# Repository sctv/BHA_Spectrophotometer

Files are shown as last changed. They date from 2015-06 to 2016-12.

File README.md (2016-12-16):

#BHA Spectrophotometer

This repo contains the designs and source files of a **DIY Spectrophotometer**. This device, based on the TSL1402R IC, can be used to do a photospectral analysis of liquid samples, such as growth curve analysis. Check out the corresponding [BHA lecture in the Syllabus](http://biohackacademy.github.io) for more information.

##Navigation the repo

 	BHA_Spectrophotometer/					main repo
 	|-- Arduino Code/Spectrophotometer/		Arduino Code
 	|-- Assembly/							Assembly guide
 	|-- Processing Code						Processing User interface code
 	BoM.md									Bill of Materials
 	Iodine Clock Reaction.pdf				Tutorial
 	Spectrophotometer-Cut-Sheet.svg			Laser cut sheet
 	Spectrophotometer-Fritzing.fzz			Wiring source
 	Spectrophotometer-Sketchup.skp			3D model
 	
##Releases

The BioHack Academy 3 release contains the following:

* 2015 BHA1 Design
* 2015 BHA2 Design
* 2016 BHA3 Design

## To Do

The To Do's are tracked using the Issues section. Please maket more suggestions by posting there.

## License

All code is licensed under GNU General Public License.

All designs are licensed under Creative Commons Contribution Share-Alike license

Copyright Waag Society

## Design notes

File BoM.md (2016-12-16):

## Bill of Materials

Make sure you have an Arduino Leonardo or equivalent microprocessor, big enough sheets of 3mm material to cut the design from and plenty of wires and M3 10 screws and nuts to assemble all the parts.

### Must have for photodiode array design

For this device you need an Arduino or equivalent microprocessor.

|No|Amount|Description|Supplier NL|Cost|
| ------------: | ------------: | :------------ | :------------ | ------------: |
|1|1|White 5mm LED|[iPrototype](https://iprototype.nl/products/components/led-lcd/ledwit), [EOO](http://www.eoo-bv.nl/index.php?_a=viewProd&productId=9088), [Hackerstore](https://www.hackerstore.nl/Artikel/257)|0.18|
|2|1|TSL1406R Photo diode array|[Mouser](http://nl.mouser.com/ProductDetail/ams/TSL1406R/?qs=owm69ILshgasXOGrAzFz%252bQ%3D%3D), [DigiKey](http://www.digikey.nl/product-detail/en/TSL1406R/TSL1406-R-ND/3095064)|22.57|
|3|1|1,000 lines/mm grating|[ipacity](http://ipacity.biedmeer.nl/Webwinkel-Product-78540591/Folie-tralie-1000-lijnen-mm-%2815-x-30-cm%29.html), [Carolina](http://www.carolina.com/physical-science-light-and-optics/diffraction-grating/755230.pr?catId=&mCat=&sCat=&ssCat=&question=diffraction+grating)|14.00|
|4|1|100 uF capacitor|[Farnell](http://nl.farnell.com/panasonic-electronic-components/eeufr1c101/cap-alu-elec-100uf-16v-rad/dp/1907228)|0.14|
|5|4|220 ohm resistor|[Farnell](http://nl.farnell.com/multicomp/mcf-0-25w-220r/resistor-carbon-film-220r-0-25w/dp/9339299?Ntt=9339299), [iPrototype](https://iprototype.nl/products/components/resistors/220R), [EOO](http://www.eoo-bv.nl/index.php?_a=viewProd&productId=7085)|0.02|
|6|1|Array of 13 right angle header pins|[iPrototype](https://iprototype.nl/products/accessoires/headers/header-male-right-angle)|0.99|
|7|1|RGB LED|[Farnell](http://nl.farnell.com/kingbright/l-154a4surkqbdzgw/led-multi-colour-rgb-5mm/dp/2290374), [iPrototype](https://iprototype.nl/products/components/led-lcd/rgbled)|0.95|

*Estimate cost*: EUR 38.85

**Alternatives**

* Photodiode arrays can be found in flat bed scanners
* CCD chips are part of cheap webcams
* Compact Discs (CDs) have 0.001 mm slits

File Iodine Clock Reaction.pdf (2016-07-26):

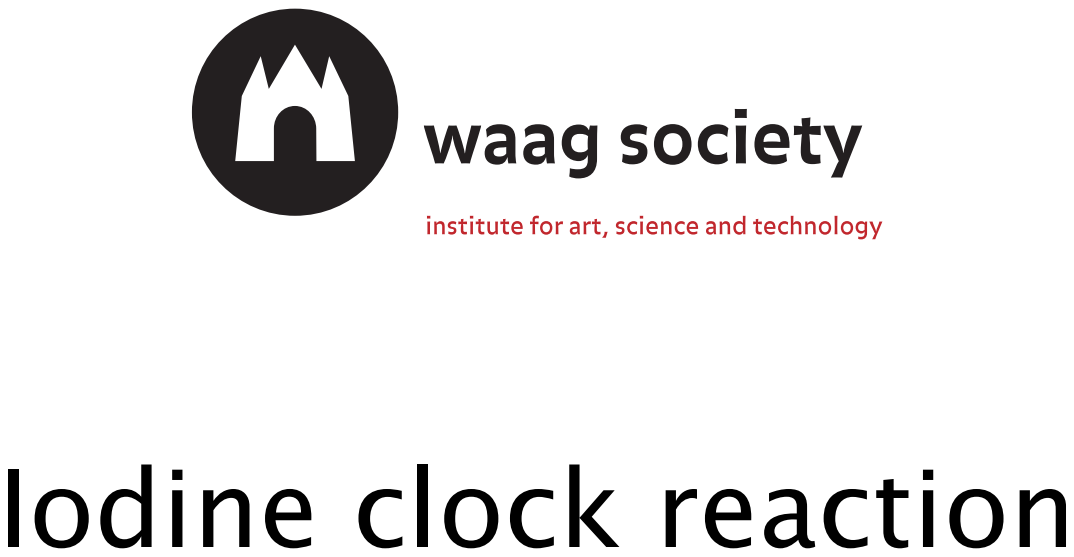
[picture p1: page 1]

Iodine clock reaction

## Consumables and Equipment

- 4x 50 mL tube
- 1000 mg Vitamin C tablet (you can also use two 500mg of course)
- Iodine (2%) availabe at a drug store
- Hydrogen peroxide (3%) also from a drug store
- Liquid Starch Solution (0.3%, so 3 grams of starch in 1 liter of heated water)
- Warm water
- Pipettes
- Plastic bag
- Safety goggles
- Marker

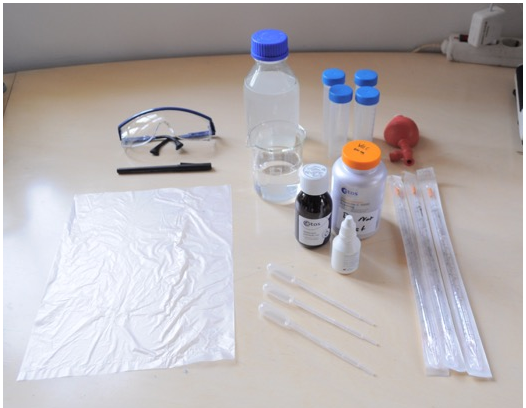
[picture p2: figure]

## Iodine clock reaction

Put on those safety goggles

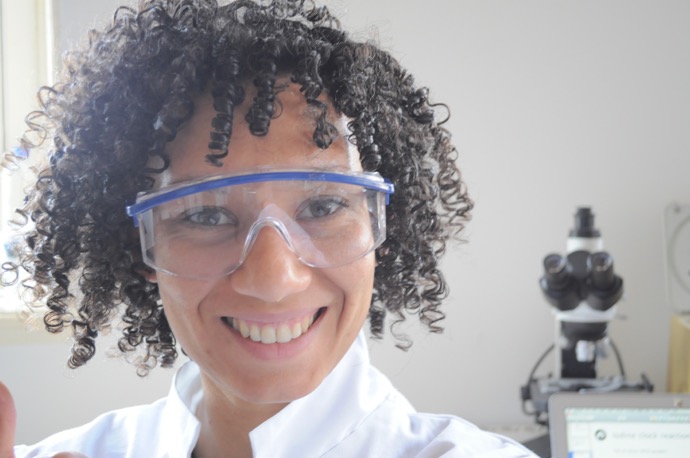
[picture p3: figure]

## Iodine clock reaction

Crush the Vitamin C tablet in a plastic bag

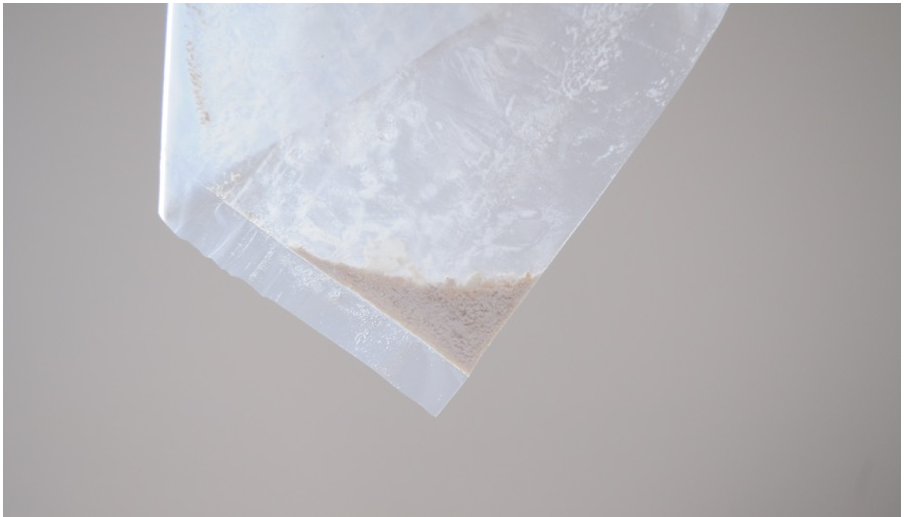
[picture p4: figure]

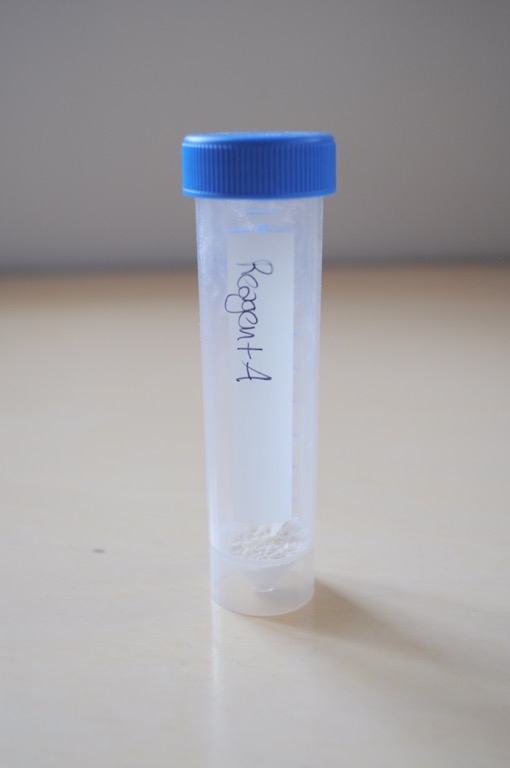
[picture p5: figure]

- Put the powder in a 50 mL tube
- label it with “Reagent A”

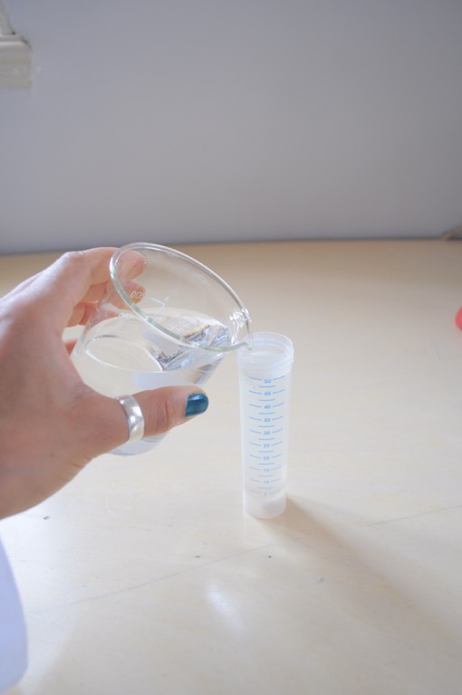
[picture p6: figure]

- Add 50 mL of warm water.
- Stir or shake for at least 30 seconds.

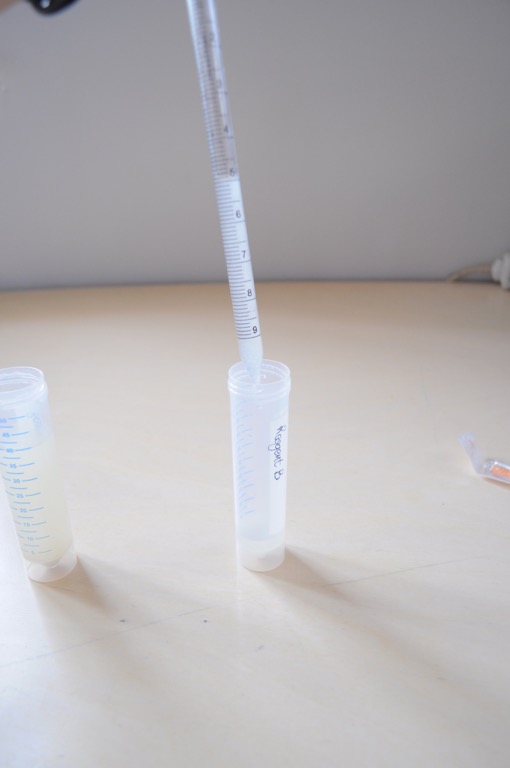
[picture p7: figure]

- Transfer 5 ml of Reagent A into a new 50 mL tube
- Label as “Reagent B”

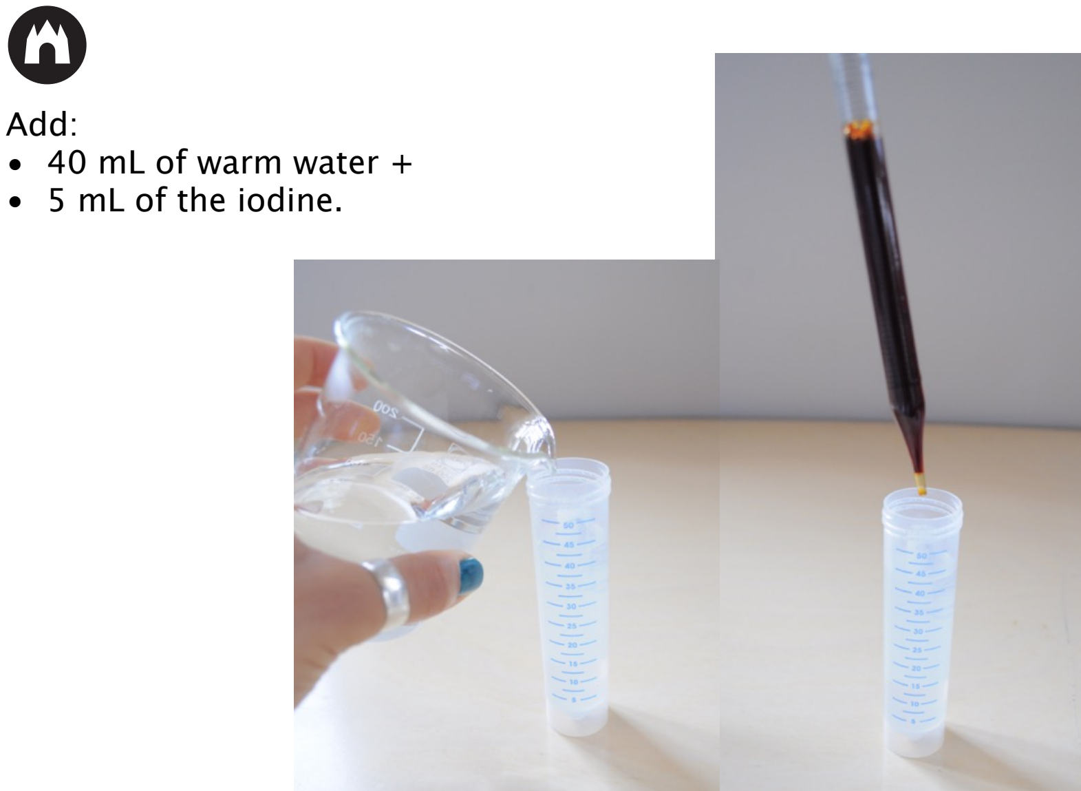
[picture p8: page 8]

Add:
- 40 mL of warm water +
- 5 mL of the iodine.

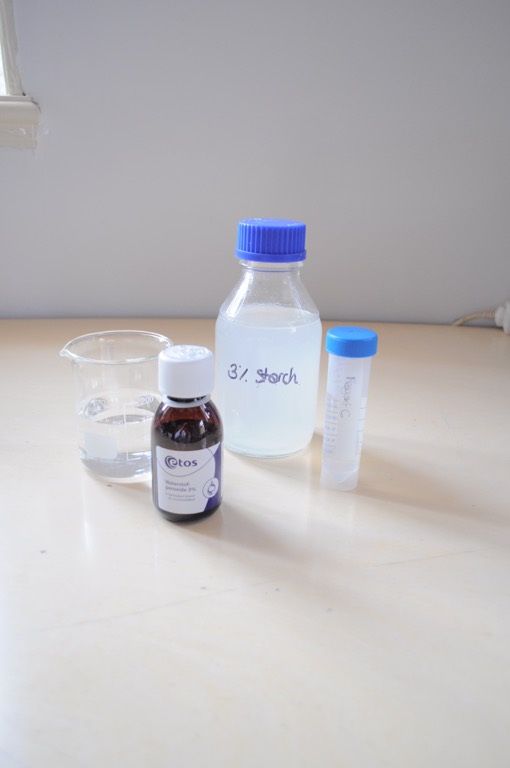
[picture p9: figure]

In the third 50 mL tube mix:
- 15 mL of warm water,
- 15 mL of the hydrogen
peroxide
- 2.5 mL of the liquid starch.

This is “Reagent C”

## Iodine clock reaction

- Mix 25 mL of Reagent C with 25 mL of Reagent B
- Immediately place in a spectrometer or just watch what happens
- Record the change to the spectrum

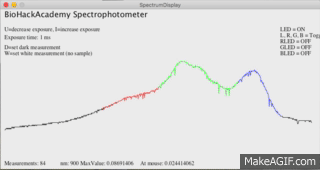
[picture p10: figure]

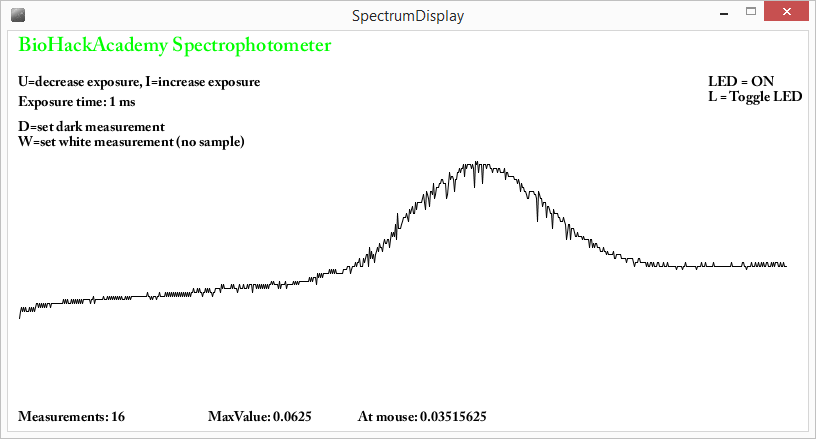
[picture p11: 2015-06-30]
Processing Code/screenshot-1.png

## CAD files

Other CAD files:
Spectrophotometer-Sketchup.skp

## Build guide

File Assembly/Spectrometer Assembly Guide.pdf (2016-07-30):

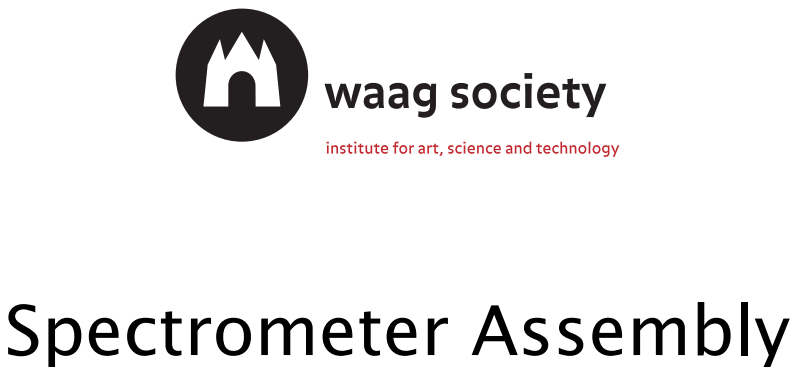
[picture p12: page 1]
Spectrometer Assembly

Wiring

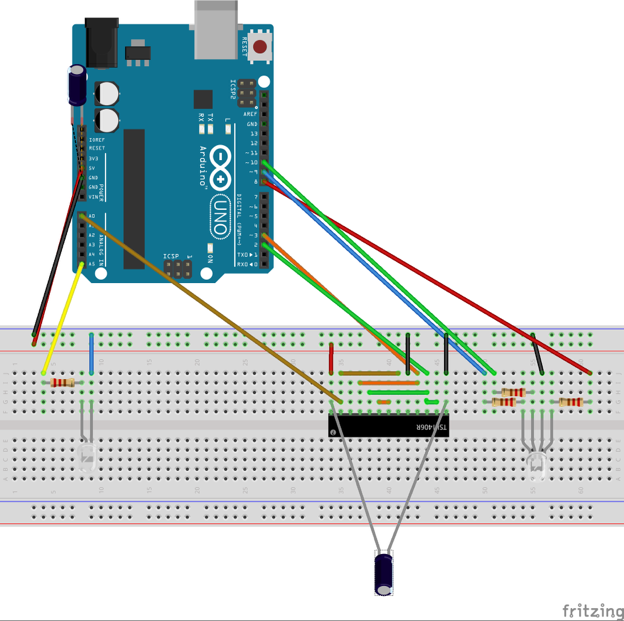
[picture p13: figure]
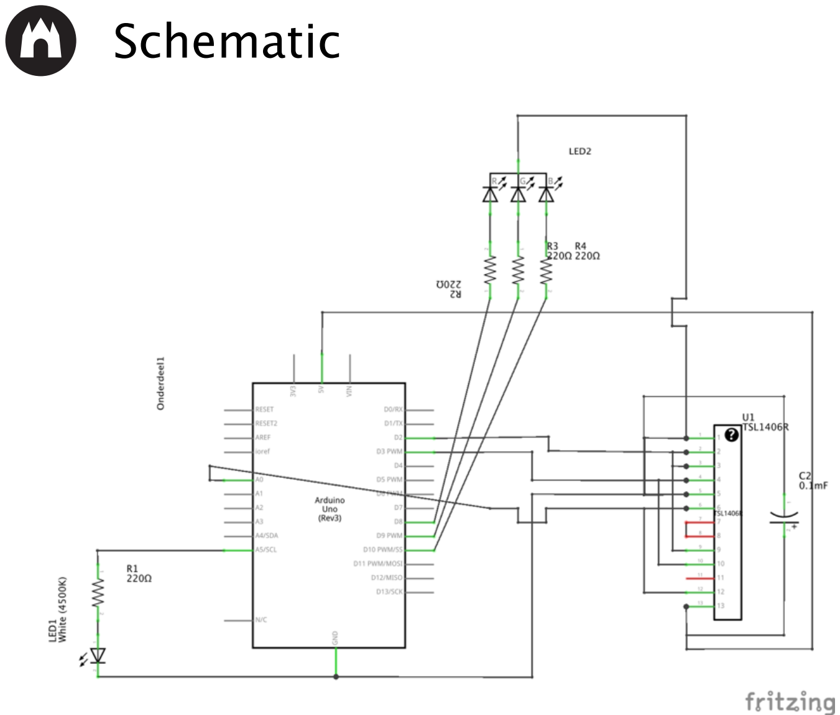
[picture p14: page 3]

Schematic

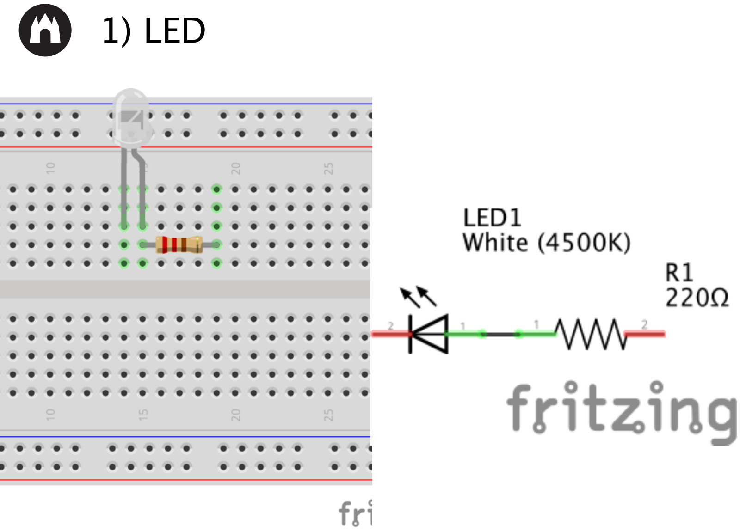
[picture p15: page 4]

1) LED

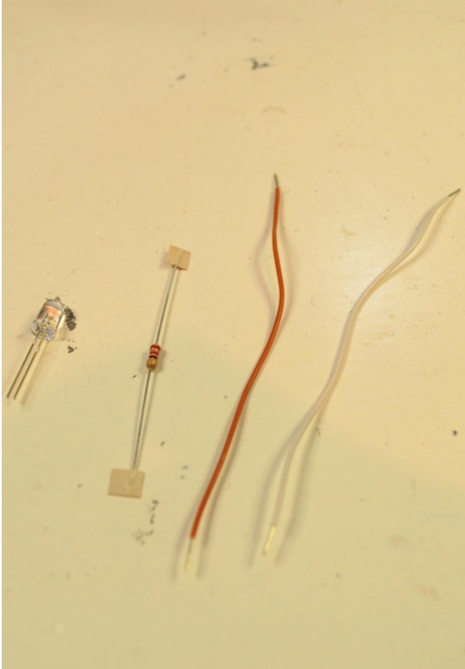
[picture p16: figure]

- 2x 10 cm wire
- White LED
- 220 Ohm resistor
- Shorten the leads

Assembly

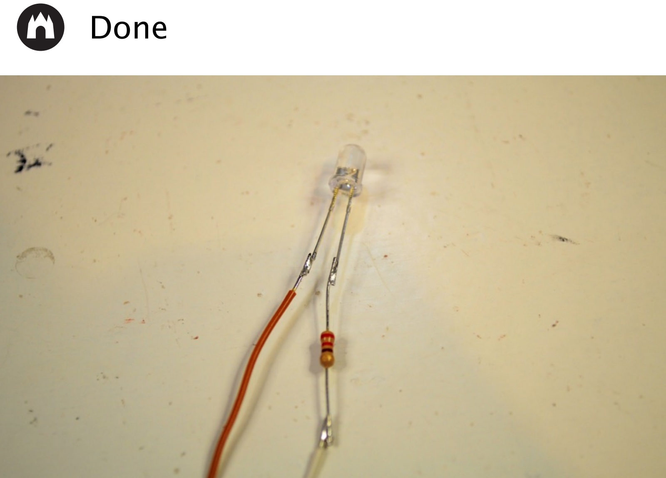
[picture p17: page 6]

Done

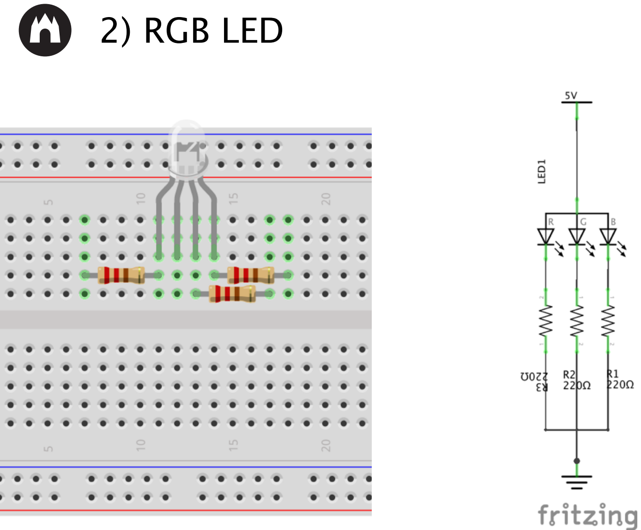
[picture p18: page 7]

2) RGB LED

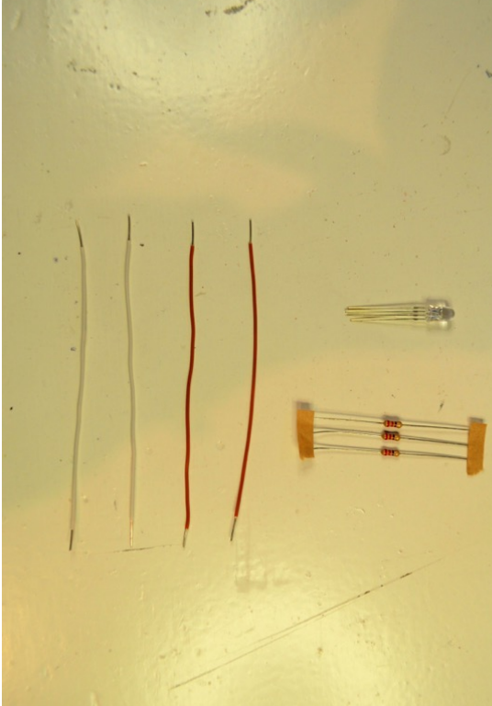
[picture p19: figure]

- 4x 10 cm wire
- 1x RGB LED
- 3x 220 Ohm resistor
- Shorten the leads

Assembly

Done

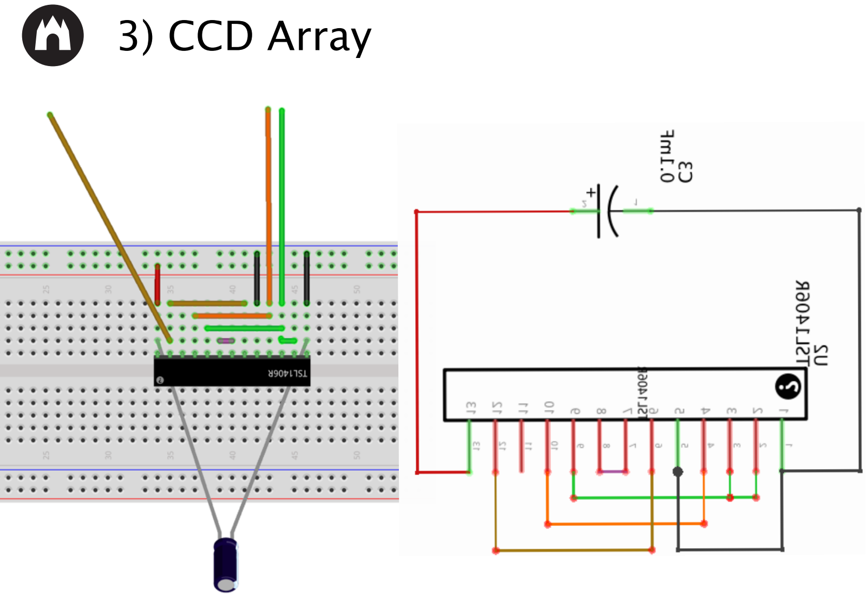
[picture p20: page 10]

3) CCD Array

Start with soldering the header pins

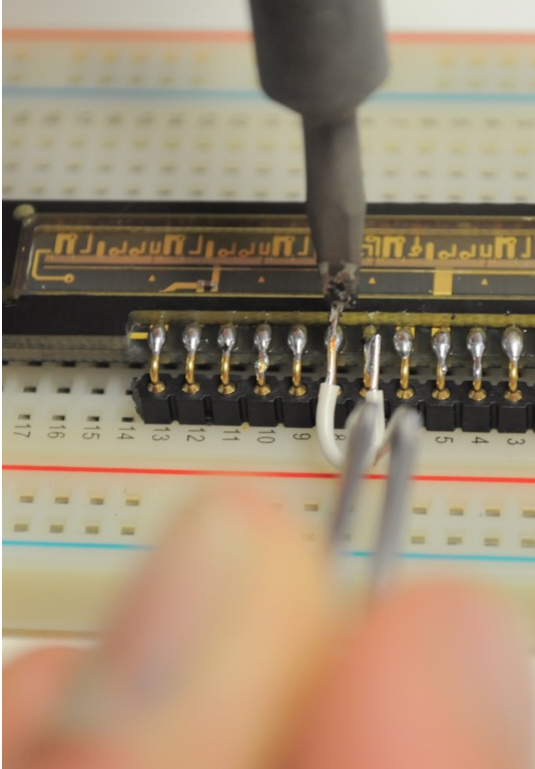
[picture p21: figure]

- 2x short wire
- 3x medium wire
- 5x 20 cm wire
- Start with connecting
- 7 and 8

Assembly

Connect 2, 3 and 9

Trick:
Dual connection

Connect 4 and 10

Connect 6 to 12

Connect 1 to 5

Connect long wires to 1, 3, 4, 12 & 13

Connect the capacitor between 1 & 13

Make sure the white mark of the capacitor is facing pin 1

- 1 to GND (-)
- 13 to Vcc (+)
- 3 to Arduino 2
- 4 to Arduino 3
- 12 to Arduino A0

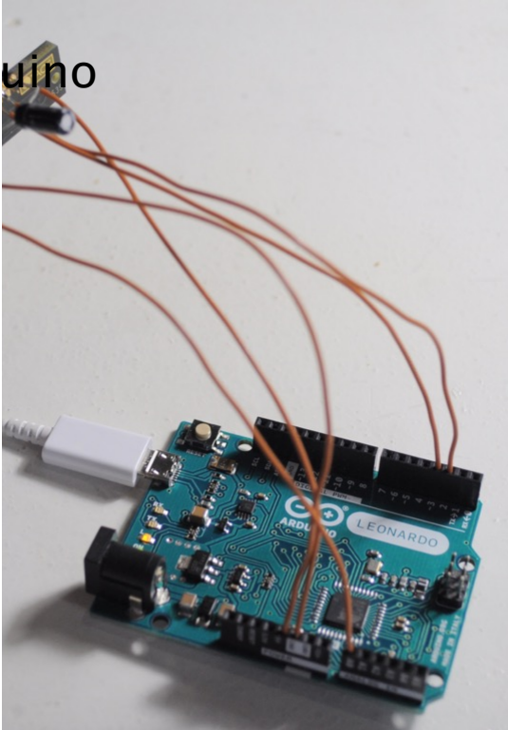
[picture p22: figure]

Connect to Arduino

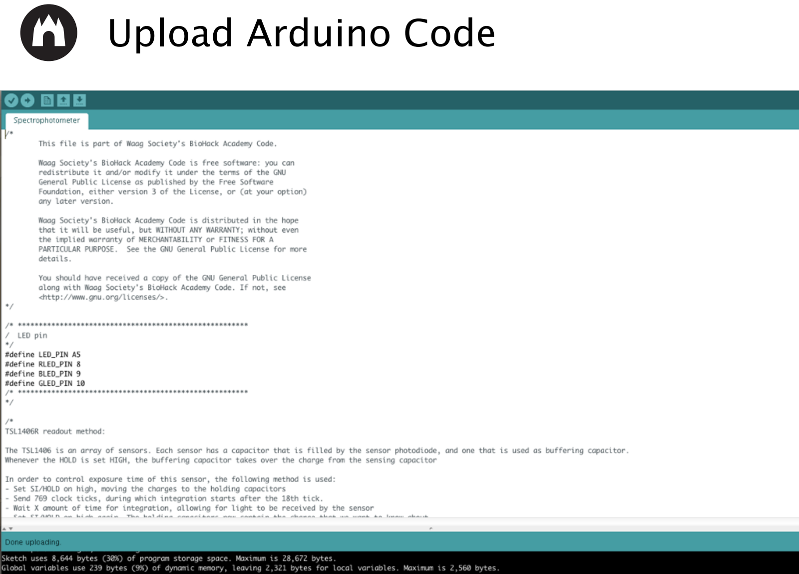
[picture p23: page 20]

Upload Arduino Code

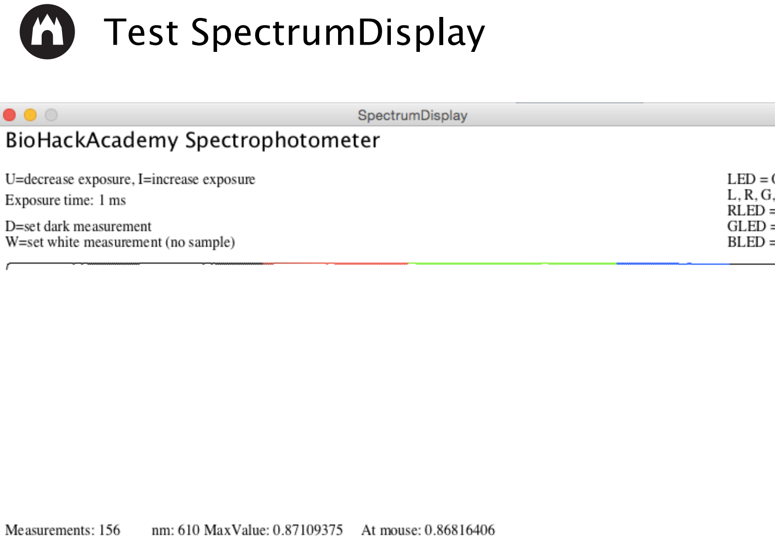
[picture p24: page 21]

Test SpectrumDisplay

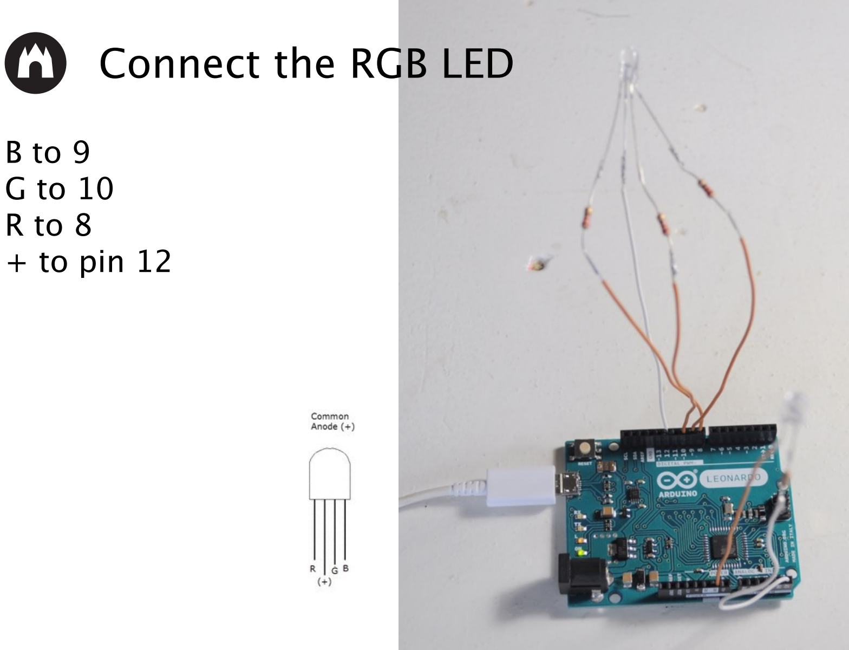
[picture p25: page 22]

B to 9
G to 10
R to 8
+ to pin 12

Connect the RGB LED

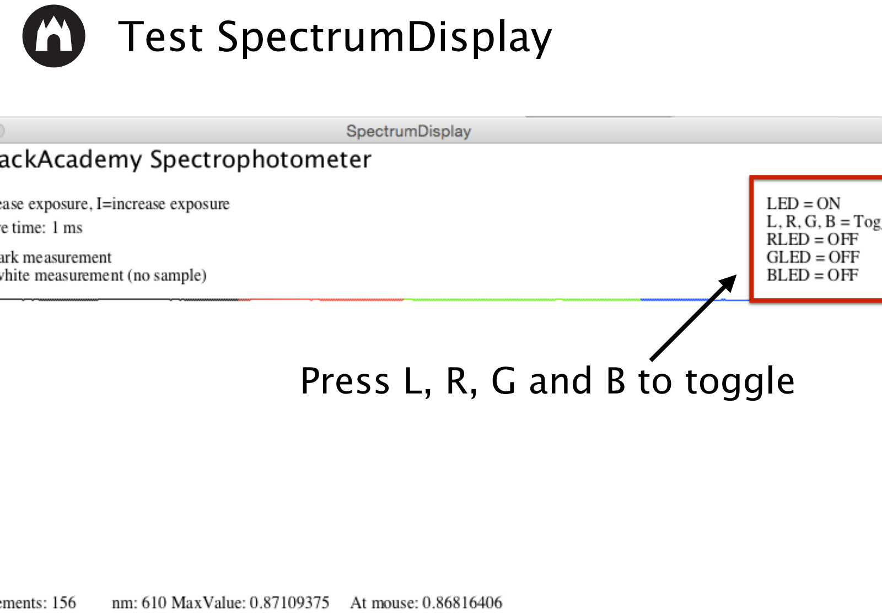
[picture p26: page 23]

Test SpectrumDisplay

Press L, R, G and B to toggle

Lasercut and assemble the box

Mount the electronics

Cut and place the grating foil

Clamp it here

Cut a piece of this

Mount the CCD array

Place the cuvette and lid

Make sure it all fits

Seal the box

Ready to measure!

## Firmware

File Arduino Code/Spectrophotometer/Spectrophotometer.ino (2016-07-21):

/*
	This file is part of Waag Society's BioHack Academy Code.

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
	You should have received a copy of the GNU General Public License
	along with Waag Society's BioHack Academy Code. If not, see 
	<http://www.gnu.org/licenses/>.
*/

/* *******************************************************
/  LED pin
*/
#define LED_PIN A5
#define RLED_PIN 8
#define BLED_PIN 9
#define GLED_PIN 10
#define onBoard_PIN 13
/* *******************************************************
*/

/*
TSL1406R readout method:

The TSL1406 is an array of sensors. Each sensor has a capacitor that is filled by the sensor photodiode, and one that is used as buffering capacitor. 
Whenever the HOLD is set HIGH, the buffering capacitor takes over the charge from the sensing capacitor 

In order to control exposure time of this sensor, the following method is used:
- Set SI/HOLD on high, moving the charges to the holding capacitors
- Send 769 clock ticks, during which integration starts after the 18th tick. 
- Wait X amount of time for integration, allowing for light to be received by the sensor
- Set SI/HOLD on high again. The holding capacitors now contain the charge that we want to know about
- Readout.

*/
class TSL1406
{
public:
  byte pin_si, pin_clk, pin_analogOut;
  int exposureTime;
  
  TSL1406(byte pin_si, byte pin_clk, byte pin_ao) {
    this->pin_si = pin_si;
    this->pin_clk = pin_clk;
    this->pin_analogOut = pin_ao;
    
    pinMode(pin_si, OUTPUT);
    pinMode(pin_clk, OUTPUT);
    pinMode(pin_ao, INPUT);
    
    exposureTime = 5;
  }
  
  void clockPulse() {
    digitalWrite(pin_clk,1);
    digitalWrite(pin_clk,0);
  }
  
  void read(int* output)
  {
    digitalWrite(pin_si,1);
    clockPulse();
    digitalWrite(pin_si,0);
    
    for (int i=0;i<769;i++) {
      clockPulse();
    }
    
    delay(exposureTime);

    digitalWrite(pin_si,1);
    clockPulse();
    digitalWrite(pin_si,0);
  
    for (int i=0;i<768;i++) {
      int val = analogRead(pin_analogOut);
      clockPulse();
      output[i] = val;
    }
 
  }
};

const byte PIN_SI = 2;
const byte PIN_CLK = 3;
const byte PIN_AO = A0;
TSL1406 sensor(PIN_SI,PIN_CLK, PIN_AO);

String buffer;

// the setup function runs once when you press reset or power the board
void setup() {
  // initialize digital pin 13 as an output.
  pinMode(onBoard_PIN, OUTPUT);

  Serial.begin(57600);
  Serial.println("Spectrophotometer v1");
  
  pinMode(LED_PIN, OUTPUT);
  pinMode(RLED_PIN, OUTPUT);
  pinMode(GLED_PIN, OUTPUT);
  pinMode(BLED_PIN, OUTPUT);
  pinMode(12, OUTPUT);
  digitalWrite(LED_PIN, 1);
  digitalWrite(RLED_PIN, 0);
  digitalWrite(GLED_PIN, 0);
  digitalWrite(BLED_PIN, 0);
  digitalWrite(12, HIGH);
}

// Print all data to Serial
void printOutput(int *data, int offset, int count)
{
  Serial.println("start");
  
  for(int i=0;i<count;i++) {
    Serial.println(data[i]);
  }
}

// Read sensor data
void readSensor(){
  int values[768];
  sensor.read(values);
  printOutput(values,0, 768); 
}

// the loop function runs over and over again forever
void loop() {
  while (Serial.available()>0) {
    char c = (char)Serial.read();
  
    if (c == '\n') {
      if (buffer.startsWith("read")) {
        readSensor();
      }
      else if(buffer.startsWith("led")) {
        int v=buffer.substring(3).toInt();
        digitalWrite(LED_PIN,v);
      }
      else if(buffer.startsWith("rled")) {
        int v=buffer.substring(4).toInt();
        digitalWrite(RLED_PIN,v);
      }
      else if(buffer.startsWith("gled")) {
        int v=buffer.substring(4).toInt();
        digitalWrite(GLED_PIN,v);
      }
      else if(buffer.startsWith("bled")) {
        int v=buffer.substring(4).toInt();
        digitalWrite(BLED_PIN,v);
      }
      else if(buffer.startsWith("exp")) {
        sensor.exposureTime = buffer.substring(3).toInt();
      }
      else {
        Serial.println("Unknown cmd.");
      }
      buffer="";
    } else buffer+=c;
  }  
 
  static byte led_val=0;  
  digitalWrite(onBoard_PIN, led_val); 
  led_val=1-led_val;
  
  delay(100);  
}

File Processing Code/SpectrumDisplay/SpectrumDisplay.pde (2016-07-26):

import processing.serial.*;

import java.text.SimpleDateFormat;
import java.util.Date;
import java.util.Calendar;

Serial port; // The serial port

int exposureTime = 1; // 1 ms
float updateSpeed = 2000; // 2000 ms
int lastSpectrumUpdate=0; // keep track of time in this variable

// LED toggle variables
boolean ledState=true;
boolean rledState=false;
boolean gledState=false;
boolean bledState=false;

// Variables containing the fonts
PFont defaultFont;
PFont titleFont;

// Serial communication buffer
String buffer;

//Mathematically the spectrometer should operate in the 400-900 nm wavelength range
//For this specific box, pixel one corresponds with 900 nm, pixel 768 corresponds with 400nm
//But should be calibrated..
int SpectrumSize = 768;
float[] rawSpectrumData, correctedSpectrumData;
float[] darkReadout, whiteReadout;
int spectrumValueIndex=0;
int spectraCount=0;

void setup() {
  
  // Create a window
  size(800, 400);
  
  // Create a font with the third font available to the system:
  defaultFont = createFont(PFont.list()[0], 14);
  titleFont = createFont(PFont.list()[4], 20);
  textFont(defaultFont);

  // List all the available serial ports:
  printArray(Serial.list());
  String portName = Serial.list()[2]; // Select port
  port = new Serial(this, portName, 57600); // Open connection

  // Initiate arrays
  correctedSpectrumData = new float[SpectrumSize];
  rawSpectrumData = new float[SpectrumSize];
  darkReadout = new float[SpectrumSize];
  whiteReadout = new float[SpectrumSize];
  // fill the array with dummy data
  for(int i=0;i<SpectrumSize;i++)
    whiteReadout[i]=1.0f;
  
  lastSpectrumUpdate=millis(); // Set the clock

  ledState=true;
  port.write("led 1\n"); // enable LED
}


void readSpectrum() {
  println("Updating spectrum");
  port.write("read\n"); // write to Serial port
}

void drawSpectrum() {
  int xstart=10, ystart=height-30;
  
  float maxVal=0.0f;
  for (int i=0;i<correctedSpectrumData.length;i++)
    maxVal = max(correctedSpectrumData[i],maxVal);
    
  float yscale = (height - 160)/maxVal;
  for (int i=1;i<correctedSpectrumData.length;i++) {
    
    float[] c = rgbForNm(nmForPixel(i));
    stroke(c[0],c[1],c[2]);
    
    line(i+xstart, ystart - correctedSpectrumData[i-1] * yscale, 
        i+xstart+1, ystart - correctedSpectrumData[i] * yscale);
  }
  
  int indexAtMousePos = max(0, min(SpectrumSize-1, mouseX - xstart));
  text("nm: " + nmForPixel(indexAtMousePos), 150, 390);
  text("At mouse: " + correctedSpectrumData[indexAtMousePos], 350, 390);
  text("MaxValue: " + maxVal, 200, 390);
}

/*
Compute correctedSpectrumData based on rawSpectrumData, whiteReadout and darkReadout
*/
void computeSpectrum() {
  for (int i=0;i<SpectrumSize;i++) {
    correctedSpectrumData[i] = (rawSpectrumData[i] - darkReadout[i]) / ( whiteReadout[i] - darkReadout[i]);
  }
}

//export the spectrum to a csv file to the sketch folder, 
//with timestamp as name
void saveSpectrum()
{
  PrintWriter output;
    
  SimpleDateFormat formatter = new SimpleDateFormat("yyyy-MM-dd-HH:mm:ss");
  Date today = Calendar.getInstance().getTime(); 
  String name = formatter.format(today);

  output = createWriter("data/" + name + ".csv");
  
  for(int i = 0; i < SpectrumSize; i++) 
  {
    output.print(correctedSpectrumData[i] + ";"); 
  }
  
  output.flush();  // Writes the remaining data to the file
  output.close(); 
}


void draw() {
  int time = millis(); // Get the current time

  // check whether it is time to do a new read out
  if (lastSpectrumUpdate + updateSpeed < time) {
    lastSpectrumUpdate=time;
    readSpectrum();
  }

  // Draw user interface
  background(255);
  text("U=decrease exposure, I=increase exposure", 10, 55);
  text("Exposure time: " + exposureTime + " ms", 10, 75);
  text("D=set dark measurement", 10, 100);
  text("W=set white measurement (no sample)", 10, 115);

  text("Measurements: " + spectraCount, 10, 390);

  text("LED = " + ( ledState ? "ON" : "OFF" ), 700, 55);
  text("L, R, G, B = Toggle LED", 700, 70);
  text("RLED = " + ( rledState ? "OFF" : "ON" ), 700, 85);
  text("GLED = " + ( gledState ? "OFF" : "ON" ), 700, 100);
  text("BLED = " + ( bledState ? "OFF" : "ON" ), 700, 115);
  
  textFont(titleFont);
  fill(0, 0, 0);
  text("BioHackAcademy Spectrophotometer", 10, 20);
  textFont(defaultFont);
  fill(0);
  
  drawSpectrum();
}


void serialEvent(Serial port) {
  while (port.available () >0) {
    char c = port.readChar();
    if (c == '\n' && buffer.length() > 0) { // read until the end of a line
      char first=buffer.charAt(0);
      if (first >= '0' && first <= '9') {
        int value = Integer.parseInt(buffer.trim()); // convert into an Integer
        rawSpectrumData[spectrumValueIndex++] = value/1024.0f;
        if (spectrumValueIndex==SpectrumSize) { // when all values have been received
          computeSpectrum();
          spectrumValueIndex=0;
          spectraCount ++;
        }
      } else if(buffer=="start") {
        spectrumValueIndex=0; // align again
      }
      buffer="";
    } else {
      buffer+=c;
    }
  }
}

void keyPressed() {
  if (key >= 'A' && key <= 'Z')
    key += 'a'-'A'; // make lowercase

  if (key == 'i' || key == 'u') {
    if (key == 'i') exposureTime += 3;
    else exposureTime -= 3;
    exposureTime = max(exposureTime,1);
    
    port.write("exp " + max(1, (int)exposureTime) + "\n");
  }

  if (key == 'l') {
    ledState=!ledState;
    port.write("led " + ( ledState ? "1" : "0" )+ "\n");
  }
  
  if (key == 'r') {
    rledState=!rledState;
    port.write("rled " + ( rledState ? "1" : "0" )+ "\n");
  }
  
  if (key == 'g') {
    gledState=!gledState;
    port.write("gled " + ( gledState ? "1" : "0" )+ "\n");
  }
  
  if (key == 'b') {
    bledState=!bledState;
    port.write("bled " + ( bledState ? "1" : "0" )+ "\n");
  }
  
  if (key == ' ') {
    readSpectrum();
  }
  
  if (key == 'd') {
    for (int i=0;i<SpectrumSize;i++)
      darkReadout[i] = rawSpectrumData[i];
  }
  
  if (key == 'w') {
    for (int i=0;i<SpectrumSize;i++)
      whiteReadout[i] = rawSpectrumData[i];
  }
  
  if (key == 's') 
  {
    println("save spectrum");
    saveSpectrum();
  }
  
}

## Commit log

2015-03-25 Cleaning up Sketch
    [CCD-Array-Spectrometer-Sketchup.skp, CCD-Array-Spectrometer-Sketchup~.skp]
2015-03-25 Cleaning up
    [CCD-Array-Spectrometer-Sketchup.skp, CCD-Array-Spectrometer-Sketchup~.skp]
2015-04-11 * Fix led holder slots
    [CCD-Array-Spectrometer-Sketchup.skp]
2015-04-12 Fritzing update
    [CCD-Array-Spectrometer-Fritzing.fzz, CCD-Array-Spectrometer-Sketchup.skp, CCD-Array-Spectrometer-Sketchup~.skp]
2015-04-23 wiring including capacitor
    [CCD-Array-Spectrometer-Fritzing.fzz]
2015-06-30 Archive BHA1
    [CCD-Array-Spectrometer-Fritzing.fzz, CCD-Array-Spectrometer-Sketchup.skp]
2016-03-06 SVG export
    [CCD-Array-Spectrometer-Sketchup.skp]
2016-04-25 RGB LED upgrade
    [CCD-Array-Spectrometer-Fritzing.fzz]
2016-06-30 Header pins added
    [CCD-Array-Spectrometer-Fritzing.fzz]
2016-07-18 Updated code based on RGB wiring
    [CCD-Array-Spectrometer-Fritzing.fzz]
2016-07-30 updated BoM
    [CCD-Array-Spectrometer-Sketchup.skp]
2016-07-30 Assembly guide
2016-11-11 clean up old versions
    [CCD-Array-Spectrometer-Fritzing.fzz, CCD-Array-Spectrometer-Sketchup.skp]
2016-12-16 BHA4 update
    [CCD-Array-Spectrometer-Fritzing.fzz, CCD-Array-Spectrometer-Sketchup.skp, Spectrophotometer-Fritzing.fzz, Spectrophotometer-Sketchup.skp]
2017-02-20 update schematic in .fzz
    [Spectrophotometer-Fritzing.fzz]

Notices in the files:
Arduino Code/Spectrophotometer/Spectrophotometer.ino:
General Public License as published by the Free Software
